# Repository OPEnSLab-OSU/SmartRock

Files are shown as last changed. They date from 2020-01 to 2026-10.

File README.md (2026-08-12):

# Smart Rock |<!-- [Updates](https://github.com/OPEnSLab-OSU/OPEnS-Lab-Home/wiki/smart-rock-updates) |--> [Wiki](https://github.com/OPEnSLab-OSU/SmartRock/wiki)
Project Leads: **Tyler Slaght**

Project Members; **Chris Milford**, **Owen Schwab**, **Max Emrich**

<!--Past Team Members **Annika Sundstorm** **Colin Hale-Brown**-->

Interested in the project? Email us at: slaghtt@oregonstate.edu

Smart rock aims to be a low cost, high accuracy, easy to use in-situ water quality measuring device. Our
goal with Smart Rock is to create an open source, low cost, and technically accessible hydrological sensor
suite. The intended result of this work allows data to be collected throughout a watershed; even in varied
and/or harsh conditions to improve system wide watershed knowledge.
Smart Rock could be used as a learning tool for students, teachers, and other citizen scientists. The
device currently costs ˜$350 in materials and takes approximately 4-8 hours to assemble and program.

Comprehensive Build Guide -> https://github.com/OPEnSLab-OSU/SmartRock/blob/master/Documentation/SmartRock_Guide-compressed.pdf

Smart Rock Paper -> https://github.com/OPEnSLab-OSU/SmartRock/blob/master/Documentation/SmartRock_Paper.pdf

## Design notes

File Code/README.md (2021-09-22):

## Software

For best results follow the table below for best code version:

Hardware Version | Software Version
------- | -------
Version 3 | Smartrock_firmware_v2.7
Version 2.5 | Smartrock_firmware_v2.5.1
Version 2.0 | Smartrock_firmware_v2.5.1

For best results use the following Arduino library versions for all versions of the code:

Board Package | Version
------ | ------
Arduino SAMD | 1.8.11
Adafruit SAMD | 1.5.7
Loom | 2.5.1

For info about installing Loom please visit the Loom [Github page](https://github.com/OPEnSLab-OSU/Loom) for details.

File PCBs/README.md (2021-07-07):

# Custom PCBs

Each Smart Rock contains three custom PCBs, the EC breakout board and OsmoPod can be found here. Information about the Hypnos Board can be found [Here](https://github.com/OPEnSLab-OSU/OPEnS-Lab-Home/wiki/Hypnos).

Board | Description
----- | -----
EC Breakout	| Module containing EC circuitry and breakout plugs for the other sensors.
OsmoPod | Module containing EC probes and MS5803 pressure/ temperature sensor.
Hypnos | Module for time, sleep, and data storage functionalities of the Smart Rock.

Please referance the correct PCB for your Smart Rock, board verions have changed as we have shipped.

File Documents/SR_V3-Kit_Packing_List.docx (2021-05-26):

Smart Rock V3 – Kit Parts List

OC | RC | Quantity | Photo | Item
| | 1 | | PVC Enclosure
| | 9 | | M3 Nut
| | 2 | | 8mm M3 Screw
| | 4 | | 10mm M3 Screw
| | 1 | | 3” Velcro Cable Tie
| | 1 | | Sled_Base
| | 1 | | Electronics_Mount
| | 1 | | Turbidity_Mount
| | 1 | | Battery_Mount
| | 1 | | Rail_Inside
| | 1 | | Rail_Outside
| | 1 | | Feather M0
| | 1 | | Hypnos
| | 1 | | EC Breakout Board
| | 1 | | 16GB Micro-SD Card
| | 1 | | Micro-SD Card to SD Card Adapter
| | 1 | | 3.3V 2200mAh Li-Po Battery
| | 1 | | Coin Cell Battery
| | 1 | | Li-Pi Battery Charger
| | 1 | | Smart Rock Faceplate
| | 2 | | Descant Packet
| | 1 | | Super Glue

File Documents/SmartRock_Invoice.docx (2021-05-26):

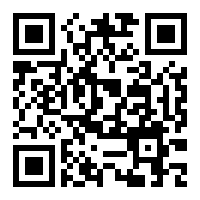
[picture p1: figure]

Smart Rock V3

Thank you for purchasing our latest revision of the Smart Rock. We have documented how to get started on the GitHub Wiki in the Operation Guide.

Contact: halebroc@oregonstate.edu

Quantity | Item

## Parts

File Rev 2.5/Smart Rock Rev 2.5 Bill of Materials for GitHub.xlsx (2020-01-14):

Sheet: Smart Rock Bill of Materials
Smart Rock Bill of Materials
Document updated/edited by: Sam Edwards and Alicia Veach
Most recent update: 10/10/2019

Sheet: Mechanical Components
Smart Rock Mechanical Components Bill of Materials
Section of Smart Rock | Smart Rock ID number | Item Description | Distributor part number | MFG part number | Quantity per 1 Smart Rock | Cost per 1 pcs | Cost Per 1 Smart Rock | Required Purchasing quantity | Cost for Required quantity | Product/site info | Notes | Total cost for one Smart Rock: | $60.24
Waterproof Case | M2-0801 | Union PVC Fittings | 457-025 | n/a | 2 | $13.93 | $27.86 | 1 | $13.93 | PVCFittingsOnline (https://www.pvcfittingsonline.com/2-1-2-sch-40-pvc-union-soc-w-buna-n-o-ring-seal-457-025.html) |  | w/o securing structure | $50.62
M3-0001 | M1-0103 | Acrylic (ends) | 8560K354 | n/a | 2 | $1.93 | $3.85 | 12"x12" | $17.34 | McMaster Carr (https://www.mcmaster.com/8560k354) | 92 mm diameter, 6 mm thickness 2 per rock =~ 1/4" thick for ordering purposes --> Cost division is approximate
 | M1-0101 | PVC Pipe | 48925K99 | n/a | 8 | $1.37 | $10.96 | 60" | $16.39 | McMasterCarr (https://www.mcmaster.com/48925k99) | qty per 1 rock is # of inches, 1pcs=1inch
Internal Structure | M2-0802 | Velcro hook squares | 9737K72 | n/a | 5 | $0.28 | $1.40 | 10 | $2.79 | McMaster (https://www.mcmaster.com/9737k72) | 5 per rock
M3-0002 | M2-0803 | Velcro loop squares | 9737K82 | n/a | 5 | $0.28 | $1.40 | 10 | $2.79 | McMaster (https://www.mcmaster.com/9737k82) | 5 per rock
 | M1-0301 | 3D printed rails | n/a | n/a | 1 | $4.00 | $4.00 | 1 | $4.00 | OPEnS (http://www.open-sensing.org/resources#form-2) | Asa print, 1 outside, 1 inside, cost comes from opens lab --> only service cost for the project.
 | M1-0102 | Acrylic (slide) | 8560K239 | n/a | 1 | $1.14 | $1.14 | 12"x12" | $9.15 | McMasterCarr (https://www.mcmaster.com/8560k239) | 50x195x4mm, laser cut, 1 per rock =~1/8"thick for ordering purposes --> Cost division is approximate
Securing Structure | M2-0901 | U-Bolt | 3035T55 | n/a | 2 | $4.81 | $9.62 | 1 | $4.81 | McMasterCarr (https://www.mcmaster.com/3035t55)
M3-0003

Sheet: Electrical Components
Smart Rock Electrical Components Bill of Materials
Section of Smart Rock | Smart Rock ID number | Item | Distributor part number | MFG part number | Quantity per 1 Smart Rock | Cost per 1 pcs | Cost per 1 Smart Rock | Required Purchasing quantity | Cost for Required quantity | Product/site info | Notes | Total cost for one Smart Rock: | $152.43
Pressure Sensor Assembly | E2-0101 | Pressure Sensor | 223-1623-5-ND | MS580302BA01-00 | 1 | $13.82 | $13.82 | 1 | $13.82 | Digikey (https://www.digikey.com/product-detail/en/te-connectivity-measurement-specialties/MS580301BA01-00/223-1623-5-ND/5277628)
E3-0001 | E2-0201 | 10k resistor | RR12P10.0KDCT-ND | RR1220P-103-D | 2 | $0.04 | $0.08 | 100 | $3.49 | Digikey (https://www.digikey.com/product-detail/en/susumu/RR1220P-103-D/RR12P10.0KDCT-ND/432854) | surface mount
 | E2-0301 | 100nF Capacitor | 1276-1007-1-ND | CL21F104ZBCNNNC | 1 | $0.03 | $0.03 | 100 | $2.03 | Digikey (https://www.digikey.com/product-detail/en/samsung-electro-mechanics/CL21F104ZBCNNNC/1276-1007-1-ND/3889093) | surface mount
Microcontroller Assembly | E2-0601 | Feather Wifi m0 |  | 2995 | 1 | $20.00 | $20.00 | 1 | $34.95 | Adafruit Product (https://www.adafruit.com/product/3061)
E3-0006 | E2-0505 | Stackable headers |  | 2830 | 2 | $0.50 | $2.00 | 1 | $0.50 | Adafruit (https://www.adafruit.com/product/2830)
 | E2-0506 | Break away male headers |  | 392 | 1 | $4.95 | $0.17 | 1 | $4.95 | Adafruit (https://www.adafruit.com/product/392) | 12 pins total needed, 360 per pack
Turbidity Sensor E3-0007 | E2-0102 | Turbidity Sensor | SEN0189 |  | 1 | $9.90 | $9.90 | 1 | $9.90 | DF Robot (https://www.dfrobot.com/product-1394.html)
pH Sensor |  | pH Sensor | SEN0169 |  | 1 | $56.90 | $56.90 | 1 | $56.90 | DF Robot (https://www.dfrobot.com/product-1110.html)
Battery | E2-1203 | Lithium-Ion Poly Battery | 328 |  | 1 | $14.95 | $14.95 | 1 | $14.95 | Adafruit Product (https://www.adafruit.com/product/328) | 3.7V, 2500mAh
Salinity assembly | E2-0103 | TDS Sensor Probe | SEN0244 |  | 1 | $12.90 | $12.90 | 1 | $12.90 | DF Robot (https://www.dfrobot.com/product-1662.html)
E3-0005
Hypnos assembly |  | n channel mosfet | DMN65D8L-7DICT-ND |  | 1 | $0.17 | $0.17 |  |  | Digikey (https://www.digikey.com/product-detail/en/diodes-incorporated/DMN65D8L-7/DMN65D8L-7DICT-ND/3677916)
$15.74 |  | p channel mosfet | DMP3099L-7DICT-ND |  | 2 | $0.33 | $0.66 |  |  | Digikey (https://www.digikey.com/products/en?keywords=DMP3099L-7DICT-ND)
 |  | 80k resistor 1% | A129833CT-ND |  | 1 | $0.10 | $0.10 |  |  | Digikey (https://www.digikey.com/product-detail/en/te-connectivity-passive-product/CRGCQ1206F82K/A129833CT-ND/8577665)
 |  | 100k resistor 1% | 311-100KCRCT-ND |  | 2 | $0.10 | $0.20 |  |  | Digikey (https://www.digikey.com/product-detail/en/yageo/RC0805FR-07100KL/311-100KCRCT-ND/730491)
 |  | 30k resistor 5% | P30KECT-ND |  | 4 | $0.10 | $0.40 |  |  | Digikey (https://www.digikey.com/product-detail/en/panasonic-electronic-components/ERJ-8GEYJ303V/P30KECT-ND/203313)
 |  | MicroSD card socket | 1660 |  | 1 | $1.95 | $1.95 |  |  | Adafruit (https://www.adafruit.com/product/1660)
 |  | DS3231 IC | DS3231SN#T&R |  | 1 | $8.77 | $8.77 |  |  | Digikey (https://www.digikey.com/products/en?keywords=DS3231SN%23T%26RCT-ND)
 |  | Push button | KMR731NG LFS |  | 2 | $0.34 | $0.68 |  |  | Digikey (https://www.digikey.com/product-detail/en/c-k/KMR731NG-LFS/CKN10687CT-ND/6035359)
 |  | Battery holder 12mm | 36-3000CT-ND |  | 1 | $0.91 | $0.91 |  |  | Digikey (https://www.digikey.com/product-detail/en/keystone-electronics/3000TR/36-3000CT-ND/1532229)
 |  | 10k resistor 1% | A130183CT-ND |  | 2 | $0.10 | $0.20 |  |  | Digikey (https://www.digikey.com/product-detail/en/te-connectivity-passive-product/CRGCQ1206J10K/A130183CT-ND/8578015)
 |  | 0.1uF capacitor | 311-1488-1-ND |  | 2 | $0.19 | $0.38 |  |  | Digikey (https://www.digikey.com/product-detail/en/yageo/CC1206KKX7R0BB104/311-1488-1-ND/2833794)
 |  | KingBright LED low current | 754-1935-1-ND |  | 2 | $0.51 | $1.02 |  |  | Digikey (https://www.digikey.com/product-detail/en/kingbright/APT2012LSECK-J3-PRV/754-1935-1-ND/5177465)
 |  | 3K ohm resistor 1% | RMCF1206FT3K00CT-ND |  | 1 | $0.10 | $0.10 |  |  | Digikey (https://www.digikey.com/product-detail/en/stackpole-electronics-inc/RMCF1206FT3K00/RMCF1206FT3K00CT-ND/2418728)
 |  | 6.2k ohm resistor 1% | 311-6.20KFRCT-ND |  | 1 | $0.10 | $0.10 |  |  | Digikey (https://www.digikey.com/product-detail/en/yageo/RC1206FR-076K2L/311-6.20KFRCT-ND/731963)
 |  | 100pF Capacitor | 399-1205-1-ND |  | 1 | $0.10 | $0.10 |  |  | Digikey (https://www.digikey.com/product-detail/en/kemet/C0805C101J5GACTU/399-1122-1-ND/411397)
 | E2-1202 | MicroSD Card with adapter |  |  | 1 | $4.99 | $4.99 | 1 | $4.99 | Amazon (https://www.amazon.com/SanDisk-Mobile-MicroSDHC-SDSDQM-B35A-Adapter/dp/B004ZIENBA?s=gateway)
 | E2-1201 | Coin cell battery |  | 380 | 1 | $0.95 | $0.95 | 1 | $0.95 | Adafruit Product (https://www.adafruit.com/product/380)

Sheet: PCBs
Smart Rock Electrical Components Bill of Materials
Section of Smart Rock | Smart Rock ID Number | Item | Quantity per Smart Rock | Cost Per 1 Smart Rock | Required Purchasing Quantity | Cost for required quantity | Product site/info | notes | Total cost for one Smart Rock: | $9.43
Pressure Sensor | E2-0701 | Pressure Sensor PCB | 1 | $0.48 | 3 | $1.45 | OSH Park
Hydro PCB | E2-0703 | Base PCB | 1 | $5.50 | 3 | $16.50 | OSH Park
Hypnos | E2-0704 | Hypnos | 1 | $3.45 | 3 | $10.35 | OSH Park

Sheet: Bulk Materials
Smart Rock Bulk Materials Bill of Materials
(materials that can not have calculated quantities per 1 Smart Rock)
Section of Smart Rock | Smart Rock ID number | Item | Distributor part number | MFG part number | Required Purchasing quantity | Cost for Required quantity | Product/site info | Notes
Waterproof Case | M1-0201 | Epoxy | N/A | N/A | 1 tube 0.85 oz | $7.17 | Amazon (https://www.amazon.com/Loctite-1919324-0-85-Fluid-Syringe-1405604/dp/B00KH62K50?hvadid=77790515638846&hvbmt=be&hvdev=c&hvqmt=e&s=gateway)
Waterproof Case | M1-0202 | Silicone Grease | N/A | 92003 | 1 tube 3 oz | $9.79 | Amazon (https://www.amazon.com/Super-Lube-92003-Lubricating-Translucent/dp/B0081JE0OO?s=gateway&srs=3044028011)
Waterproof Case | M1-0203 | PVC Cement | N/A | 31133 | 1can 16oz | $16.43 | Amazon (https://www.amazon.com/Oatey-31133-Weather-Cement-32-Ounce/dp/B000BVS08C?th=1)
Waterproof Case | M1-0204 | PVC Primer | 18815K51 | N/A | 1can 8oz | $6.07 | McMasterCarr (https://www.mcmaster.com/18815k51)
Pressure Sensor | E1-0201 | Lead Free Solder Paste | TS391SNL-ND | TS391SNL | 1 | $16.95 | Digikey (https://www.digikey.com/product-detail/en/chip-quik-inc/TS391SNL/TS391SNL-ND/7802215) | 12 month shelf life
Solder stock | E1-0202 | Rosin Flux-Core Solder | 7659A41 |  | 1 | $4.81 | McMaster-Carr (https://www.mcmaster.com/7659a41)
Wiring | E1-0101 | Female dupont wire |  |  | 1 pack | $9.99 | Amazon (https://www.amazon.com/KABUDA-Multicolored-Dupont-Breadboard-Arduino/dp/B07QXXMWRZ?s=gateway) | 40 pin male, 40 pin female
Battery |  | Battery Charger | 1304 |  | 1 | $5.95 | Adafruit (https://www.adafruit.com/product/1304)
Internal Structure | M1-0205 | Super Glue |  | 7805001 | 1 0.53oz container | $2.99 | #VALUE! (https://www.amazon.com/Gorilla-Super-Glue-Gram-Clear/dp/B001IY82FM?hvadid=193151859311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)
 |  |  |  |  |  | $71.21

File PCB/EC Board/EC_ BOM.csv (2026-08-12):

Qty | Value | Device | Package | Parts | Description | ARROW_PART_NUMBER | ARROW_PRICE-STOCK | AVAILABILITY | CATEGORY | COPYRIGHT | CURRENT_RATING | DATASHEET | DESCRIPTION | FORWARD_CURRENT | FORWARD_VOLTAGE | HEIGHT | MANUFACTURER | MANUFACTURER_NAME | MANUFACTURER_PART_NUMBER | MATERIAL_CORE | MF | MFR_NAME | MOUSER_PART_NUMBER | MOUSER_PRICE-STOCK | MP | MPN | OPERATING_TEMP | OPERATING_TEMPERATURE | PACKAGE | PACKAGE_SIZE | PACKAGE_TYPE | PART_STATUS | POPULARITY | PRICE | RATING | REFDES | REVERSE_VOLTAGE | ROHS | ROHS_COMPLIANT | SERIES | SUB-CATEGORY | SUBCATEGORY | TEMPERATURE_COEFFICIENT | THERMALLOSS | TOLERANCE | TYPE | VOLTAGE_RATING | ZENER_VOLTAGE
3 |  | PINHD-1X4 | 1X04 | JP1, JP2, JP3 | PIN HEADER |  |  |  |  |  |  |  |  |  |  |  |  |  |  |  |  |  |  |  |  |  |  |  |  |  |  |  | 91
5 | 100k | R-US_CHIP-0402(1005-METRIC) | RESC1005X40 | R3, R6, R13, R14, R15 | Resistor Fixed - ANSI |  |  |  | Resistor |  |  |  |  |  |  |  |  |  |  |  |  |  |  |  |  |  |  |  |  |  |  |  |  |  |  |  |  |  |  |  | Fixed
4 | 10k | R-US_CHIP-0402(1005-METRIC) | RESC1005X40 | R1, R5, R11, R12 | Resistor Fixed - ANSI |  |  |  | Resistor |  |  |  |  |  |  |  |  |  |  |  |  |  |  |  |  |  |  |  |  |  |  |  |  |  |  |  |  |  |  |  | Fixed
1 | 10k | R-US_CHIP-1206(3216-METRIC) | RESC3216X70 | SHUNT | Resistor Fixed - ANSI |  |  |  | Resistors |  |  |  | Chip Resistor 3.20 X 1.60 X 0.70 mm body 1206(3216-METRIC) Package |  |  |  |  |  |  |  |  |  |  |  |  |  |  |  |  | 1206 | Surface Mount
6 | 1k | R-US_CHIP-0402(1005-METRIC) | RESC1005X40 | R2, R4, R7, R8, R9, R10 | Resistor Fixed - ANSI |  |  |  | Resistor |  |  |  |  |  |  |  |  |  |  |  |  |  |  |  |  |  |  |  |  |  |  |  |  |  |  |  |  |  |  |  | Fixed
2 | 1nF | C_CHIP-0402(1005-METRIC) | CAPC1005X60 | C13, C14 | Capacitor - Generic |  |  |  | Capacitor
16 | 1uF | C_CHIP-0402(1005-METRIC) | CAPC1005X60 | C1, C2, C3, C4, C9, C10, C11, C12, C15, C16, C17, C18, C19, C20, C21, C22 | Capacitor - Generic |  |  |  | Capacitor
2 | 4.7uF | C_CHIP-0402(1005-METRIC) | CAPC1005X60 | C7, C8 | Capacitor - Generic |  |  |  | Capacitor
1 | 68 uH | L_CHIP-0805(2012-METRIC) | INDC2009X120 | L1 | Inductor Fixed - Generic |  |  |  | Inductors |  |  |  | Chip 2.00 X 0.90 X 1.20 mm body 0805(2012-METRIC) |  |  |  |  |  |  |  |  |  |  |  |  |  |  |  |  | 0805 | Surface Mount
1 | 74AUP1T08GWH | 74AUP1T08GWH | SOT65P212X110-5N | IC1 | 74AUP1T08 - Low-power 2-input AND gate with voltage-level translator@en-us | 74AUP1T08GWH | https://www.arrow.com/en/products/74aup1t08gwh/nexperia?region=nac |  |  |  |  |  | 74AUP1T08 - Low-power 2-input AND gate with voltage-level translator@en-us |  |  | 1.1mm |  | Nexperia | 74AUP1T08GWH |  |  |  | 771-74AUP1T08GWH | https://www.mouser.co.uk/ProductDetail/Nexperia/74AUP1T08GWH?qs=chTDxNqvsynKkpBm9IAgCA%3D%3D
2 | 865090640004CAP_WCAP-ASLU_04P0X05P5_WRE-L | 865090640004CAP_WCAP-ASLU_04P0X05P5_WRE-L | CAP_WCAP-ASLU_04P0X05P5_WRE-L | C5, C6 |  |  |  |  |  | Copyright (C) 2024 Ultra Librarian. All rights reserved. |  |  |  |  |  |  |  |  | 865090640004 |  |  | Wurth Electronics
1 | ADAFRUIT_FEATHERWING | ADAFRUIT_FEATHERWING | ADAFRUIT_FEATHERWING | MS1
1 | ADS1115IDGSRDGS0010A_L | ADS1115IDGSRDGS0010A_L | DGS0010A_L | U2 |  |  |  |  |  | Copyright (C) 2024 Ultra Librarian. All rights reserved. |  |  |  |  |  |  |  |  | ADS1115IDGSR |  |  | Texas Instruments |  |  |  |  |  |  |  |  |  |  |  |  |  | RefDes |  |  |  |  |  |  |  |  |  | TYPE
1 | CD4060BPWR | CD4060BPWR | CD4060BPWR | U4
2 | DIODE_1N4004_DO41-10 | DIODE_1N4004_DO41-10 | DO41-10 | D1, D2 | Diode Rectifier - Popular Parts |  |  |  | Diode |  |  | https://www.onsemi.com/pdf/datasheet/1n4001-d.pdfv | Diode 400 V 1A Through Hole DO-41 | 1 A | 1.1 V |  | onsemi |  |  |  |  |  |  |  |  | 1N4004 |  | -55°C ~ 175°C |  | DO-41 | Through Hole | Obsolete |  |  |  |  | NA | Compliant |  | 1N4004 |  | Rectifiers |  |  |  | Single Diodes |  | NA
1 | MAX4678EUE+ | MAX4678EUE+ | SOP65P640X110-16N | U5
2 | OP747ARUZ-REELRU_14_ADI | OP747ARUZ-REELRU_14_ADI | RU_14_ADI | U1, U10 |  |  |  |  |  | Copyright (C) 2024 Ultra Librarian. All rights reserved. |  |  |  |  |  |  |  |  | OP747ARUZ-REEL |  |  | Analog Devices Inc
1 | PINHD-1X06_1X06M | PINHD-1X06_1X06M | 1X06 | U$1
1 | TPS60400DBVR | TPS60400DBVR | SOT95P280X145-5N | U6 | Unregulated 60mA charge pump Voltage Inverter |  |  | Unavailable |  |  |  |  | 60mA Charge Pump Voltage Inverter with Variable Switching Frequency 5-SOT-23 -40 to 85 |  |  |  |  |  |  |  | Texas Instruments |  |  |  | TPS60400DBVR |  |  |  | SOT-23-5 Texas Instruments |  |  |  |  | None
3 | US1G-E3/61T | DIODE_US1G-E3/61T_SMA | DIOM5226X290N | D9, D10, D11 | Diode Rectifier - Popular Parts |  |  |  | Diode |  |  | https://www.vishay.com/docs/88768/us1_test_dcicons.pdf | Diode 400 V 1A Surface Mount DO-214AC (SMA) | 1A | 1V |  | Vishay General Semiconductor - Diodes Division |  |  |  |  |  |  |  |  | US1G-E3/61T |  | -55°C ~ 150°C |  | SMA | Surface Mount | Active |  |  |  |  | 400V | Compliant |  | US1 |  | Rectifiers |  |  |  | Fast Recovery Rectifiers |  | NA

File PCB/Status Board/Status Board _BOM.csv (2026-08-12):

Reference Designators | Quantity | Description | Package | Value | Manufacturer | Manufacturer Part Number | Vendor | Vendor Part Number | Top/Bottom
 | 1 | Board | Board
C1, C2 | 2 | Capacitor - Generic | CAPC2012X110 | 1uF |  |  |  |  | Top
C5 | 1 | Capacitor - Generic | CAPC2012X110 | 100nF |  |  |  |  | Top
I2C#1-SOLDERPADS, LED_SOLDERPADS | 2 |  | 1X04 | PINHD-1X04_1X04M |  |  |  |  | Top
LED1_ALWAYS-ON, LED2_READING, LED3_BLUETOOTH_READING | 3 |  | LED_LSM0805_2P0X1P25X0P8_VCC | LSM0805543VLED_LSM0805_2P0X1P25X0P8_VCC |  |  |  |  | Top
R1, R2, R3 | 3 | Resistor Fixed - Generic | RESC2012X65 | 2.2k |  |  |  |  | Top
R5 | 1 | Resistor Fixed - Generic | RESC2012X65 | 10k |  |  |  |  | Top
REED_SWITCH_HOLE | 1 |  | 1X02 | PINHD-1X02_1X02M |  |  |  |  | Top
U2 | 1 |  | MS5803-02BA01_TEC | MS580302BA01-00MS5803-02BA01_TEC |  |  |  |  | Top
U3 | 1 | Check availability | PHODET_VCNL4020 | VCNL4020-GS08 |  |  |  |  | Top

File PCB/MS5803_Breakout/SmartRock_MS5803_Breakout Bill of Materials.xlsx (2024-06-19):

EAGLE Board # | Part | Part Number | Footprint/Package | Quantity/Board | Source (Link)
U1 | Pressure/Temp Sensor | MS580302BA01-00 | 8-SMD Module | 1 | Digikey (https://www.digikey.com/en/products/detail/te-connectivity-measurement-specialties/MS580302BA01-00/5277629)
C1 | 0.1 uF Ceramic Cap | CL21F104ZBANNNC | 0805 (2012 Metric) | 1 | Digikey (https://www.digikey.com/en/products/detail/samsung-electro-mechanics/CL21F104ZBANNNC/3889200)

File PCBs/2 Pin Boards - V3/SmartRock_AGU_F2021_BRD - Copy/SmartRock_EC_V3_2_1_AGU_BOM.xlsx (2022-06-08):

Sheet: BOM
Board Label | Value | Item Description | Quantity Given | Quantity per Device | Cost per Unit | Cost per Device | Product Site | Manufacturer ID | Packaging/Case | Type | Notes | Alternative Source
JP1 | 12 Pin (Female) | CONN HDR 12POS 0.1 TIN PCB | 1 | 1 | $0.78 |  | Digikey (https://www.digikey.com/en/products/detail/sullins-connector-solutions/PPTC121LFBN-RC/807231) | S6100-ND | Tray
JP2 + JP3 | 16 Pin (Female) | CONN HDR 16POS 0.1 TIN PCB | 1 | 1 | $0.98 |  | Digikey | S7014-ND | Tray
JP5 | 3 Pin (Male) | CONN HEADER VERT 3POS 2.54MM | 1 | 1 | $0.13 |  | Digikey (https://www.digikey.com/en/products/detail/w%C3%BCrth-elektronik/61300311121/4846825) | 732-5316-ND | Tray |  | OOS
CN1 | 2 Pin 2.5mm JST | CONN HEADER VERT 2POS 2MM | 1 | 1 | $0.17 |  | Digikey (https://www.digikey.com/en/products/detail/jst-sales-america-inc/B2B-PH-K-S(LF)(SN)/926611) | 455-1704-ND | Bulk |  | OOS
CN2 | 3 Pin 2.5mm JST | CONN HEADER VERT 3POS 2MM | 1 | 1 | $0.19 |  | Digikey (https://www.digikey.com/en/products/detail/jst-sales-america-inc/B3B-PH-K-S-LF-SN/926612) | 455-1705-ND | Bulk |  | OOS
CN3 | 4 Pin 2.5mm JST | CONN HEADER VERT 4POS 2MM | 1 | 1 | $0.24 |  | Digikey (https://www.digikey.com/en/products/detail/jst-sales-america-inc/B4B-PH-K-S-LF-SN/926613) | 455-1706-ND | Bulk |  | OOS
U1 | ADS1115 | IC ADC 16BIT SIGMA-DELTA 10VSSOP | 1 | 1 | $6.38 |  | Digikey (https://www.digikey.com/en/products/detail/texas-instruments/ADS1115IDGST/2123298) | IC ADC 16BIT SIGMA-DELTA 10VSSOP | Cut Tape/VSSOP |  | OOS
U2 | 3.3V Inverter | IC REG CHARG PUMP INV 60MA SOT23 | 1 | 1 | $1.14 |  | Digikey (https://www.digikey.com/en/products/detail/texas-instruments/TPS60400DBVR/1672052) | 296-27004-1-ND - Cut Tape | Cut Tape/SOT-753 |  | OOS
U3 | Op-Amp | IC OPAMP JFET 4 CIRCUIT 14DIP | 1 | 1 | $0.85 |  | Digikey (https://www.digikey.com/en/products/detail/texas-instruments/TL074CN/277423) | 296-1777-ND | Tube/14-PDIP |  | OOS
S1 | SPDT Switch | SWITCH SLIDE SPDT 200MA 30V | 1 | 1 | $0.76 |  | Digikey (https://www.digikey.com/en/products/detail/e-switch/EG1218/101726) | EG1903-ND | Bulk
D1,D2,D3,D4,D5 | 1N4001 Diodes |  |  |  |  |  |  |  |  |  | Good to Go
C1,C2,C3 | 100nF
C4,C5,C6,C7,C8,C9,C10 | 1uF
R1,R4,R6,R17 | 1k |  |  |  |  |  | Digikey (https://docs.google.com/spreadsheets/d/1rMLxxit3fiBuBLfVr-LG5nceliVDEqr13rMm8BmzxTA/edit) |  |  |  | Already Thick Film
R5 | 2k |  |  |  |  |  | Digikey (https://www.digikey.com/en/products/detail/yageo/RC1206JR-072KL/732183) |  |  |  | Already Thick Film
R8,R11,R18,R19 | 4.7k |  |  |  |  |  | Digikey (https://www.digikey.com/en/products/detail/yageo/RC1206FR-074K7L/731834) |  |  |  | Already Thick Film
R10 | 5k(4.99k) |  |  |  |  |  | Digikey (https://www.digikey.com/en/products/detail/vishay-dale/RCS12064K99FKEA/10059723) |  |  |  | Updated to Thick Film
R2,R7,R9,R14,R15 | 10k |  |  |  |  |  |  |  |  |  | Already Thick Film
R3 | 22k |  |  |  |  |  |  |  |  |  | Already Thick Film
LED1,LED2,LED3

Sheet: OPEnS Order Format
Date Needed | Ship To | Requester | Source | Description | Units | Part Number | Price/unit | Total | Purpose: X for Y | Notes | Project | Alternative Suppliers | Order Date
 | the Lab | Cameron W |  |  |  |  |  |  |  |  | SmartRock

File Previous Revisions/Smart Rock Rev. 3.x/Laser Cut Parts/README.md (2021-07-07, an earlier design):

## Laser Cut Parts

For the construction of one Smart Rock you need one of each of these parts. They are laser cut from extruded acrylic sheets.

Part | Material Thickness 
------ | ------
Sensor_Mount | 1/4"
Sled_Base | 1/8"
Electronics_Mount | 1/8"
Turbidity_Mount | 1/8"
MG5803_Shield | 1/16"

If your Smart Rock uses a 3D Printed rail please referance the for files marked Version 3. Otherwise use the files marked Version 3.1

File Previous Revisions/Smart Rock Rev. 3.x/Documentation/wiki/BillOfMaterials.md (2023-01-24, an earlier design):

# Bill Of Materials

This is the complete bill of materials for the different kit types. For info about the materials and assembly of "in house" parts please visit their corresponding wiki pages.

Kits | Type
---- | ----
A | Fully Assembled
B | To be Assembled
C | In house parts only

**Mechanical**

_For laser cut parts, the links provided are for raw material used. Not the part itself._

Item Description | Notes | Quantity per 1 SR | Part Number | Dist. Website | In kits 
------ | ------ | ------ | ------- | ------ | ------ 
Sled_Base | Laser cut from 1/8" extruded acrylic. | 1 | #### | [McMasterCarr](https://www.mcmaster.com/8589K43/) | A,B,C
Electronics_Mount | Laser cut from 1/8" extruded acrylic. | 1 | #### | [McMasterCarr](https://www.mcmaster.com/8589K43/) | A,B,C
Turbidity_Mount | Laser cut from 1/8" extruded acrylic. | 1 | #### | [McMasterCarr](https://www.mcmaster.com/8589K43/) | A,B,C
3" Velcro Cable Tie |  | 1 | 4330221319 | [Amazon](https://www.amazon.com/dp/B00QMMKY8I/) | A,B
Battery_Mount | 3D Printed | 1 | #### |  | A,B,C
Turbidity_Cover | 3D Printed | 1 | #### |  | A,B,C
Rail_Outside | 3D Printed | 1 | #### |  | A,B,C
Rail_Inside | 3D Printed | 1 | #### |  | A,B,C
8mm M3 Screw |  | 2 | 91292A112 | [McMasterCarr](https://www.mcmaster.com/91292a112) | A,B
10mm M3 Screw |  | 4 | 91292A113 | [McMasterCarr](https://www.mcmaster.com/91292A113/) | A,B
M3 Nut |  | 10 | 91828A211 | [McmasterCarr](https://www.mcmaster.com/91828A211/) | A,B

**Electrical**

Item Description | Notes | Quantity per 1 SR | Part Number | Dist. Website | In kits 
------ | ------ | ------ | ------- | ------ | ------ 
Feather M0 Basic Proto | Microcontroller | 1 | 2772 | [Adafruit](https://www.adafruit.com/product/2772) | A,B
Hypnos Board | Data logging, system power, real time clock. | 1 | #### |  | A,B,C
EC Breakout Board | Main Board | 1 | #### |  | A,B,C
MicroSD Card with adapter | For storing data in Hypnos. | 1 | #### | [Amazon](https://www.amazon.com/SanDisk-Mobile-MicroSDHC-SDSDQM-B35A-Adapter/dp/B004ZIENBA/) | A,B
CR1220 Coin Cell | For keeping time when battery is removed. | 1 | 54ZU79 | [Grainger](https://www.grainger.com/product/GRAINGER-APPROVED-1220-54ZU79) | A,B
Battery Charger | Charge lipo battery cell | 1 | 1304 | [Adafruit](https://www.adafruit.com/product/1304) | A,B
Lithium Ion Battery | 3.7V 2200mAh | 1 | 1781 | [Adafruit](https://www.adafruit.com/product/1304) | A,B
3-pin JST Cable | 100mm long | 1 | 4336 | [Adafruit](https://www.adafruit.com/product/4336) | A,B
Turbidity Breakout Board | Comes with turbidity sensor | 1 |  | [DFRobot]() | A,B

**Acrylic Face Plate**

Item Description | Notes | Quantity per 1 SR | Part Number | Dist. Website | In kits 
------ | ------ | ------ | ------- | ------ | ------ 
Acrylic_Faceplate | Laser cut from 1/4" extruded acrylic. | 1 | #### | [McMasterCarr](https://www.mcmaster.com/8560K357/) | A,B,C
OsmoPod | MS5803 and EC | 1 | #### |  | A,B,C
Turbidity Sensor |  | 1 | SEN0189 | [DF Robot](https://www.dfrobot.com/product-1394.html) | A,B

**PVC Enclosure**

Item Description | Notes | Quantity per 1 SR | Part Number | Dist. Website | In kits 
------ | ------ | ------ | ------- | ------ | ------ 
PVC Pipe (Quantity in inches) | 2.5" pipe | 4.125 | 5AFJ8 | [Grainger](https://www.grainger.com/product/GRAINGER-APPROVED-Pipe-5AFJ8?) | A,B
PVC Union Fitting | Only part of the fitting is used, cemented onto pipe | 1 | 457-025 | [SupplyHouse](https://www.supplyhouse.com/Spears-457-025-2-1-2-PVC-Sch-40-Socket-Union-w-Buna-N-O-ring) | A,B
PVC Cap Fitting | Cemented onto pipe | 1 | 447-025 | [SupplyHouse](https://www.supplyhouse.com/Spears-447-025-2-1-2-PVC-Schedule-40-Cap) | A,B

**Assembly, Calibration, and Deployment**

Item Description | Notes | Quantity per 1 SR | Part Number | Dist. Website | In kits 
------ | ------ | ------ | ------- | ------ | ------ 
Super Glue |
30 mL Cups |
3 mL Pipette
DI Rinse Pouch |
10 μS/cm calibration pouch |
447 μS/cm calibration pouch |
1213 μS/cm calibration pouch |
Desicant Packets |

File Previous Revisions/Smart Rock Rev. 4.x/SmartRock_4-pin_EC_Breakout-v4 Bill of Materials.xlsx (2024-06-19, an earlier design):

EAGLE Board # | Part | Part Number | Footprint/Package | Quantity/Board | Source (Link)
U2,U3,U4 | Quad OPAMP IC | TL074CPWR | 14TSSOP | 3 | Digikey (https://www.digikey.com/en/products/detail/texas-instruments/TL074CPWR/378454)
U1 | Binary Counter IC | CD4060BPWR | 16TSSOP | 1 | Digikey (https://www.digikey.com/en/products/detail/texas-instruments/CD4060BPWR/525925)
U5 | 16 bit ADC IC | ADS1115BQDGSRQ1 | 10VSSOP | 1 | Digikey (https://www.digikey.com/en/products/detail/texas-instruments/ADS1115BQDGSRQ1/6575621)
U6+ | Charge Pump Inverter IC | MAX660MX/NOPB | 8SOIC | 1 | Digikey (https://www.digikey.com/en/products/detail/texas-instruments/MAX660MX-NOPB/413263)
C1,C2 | 1 uF Electrolytic Cap | UPS1H010MDD1TD | Radial, Can (though hole) | 2 | Digikey (https://www.digikey.com/en/products/detail/nichicon/UPS1H010MDD1TD/4319731)
C3, C5 | 100 uF Electrolytic Cap | 10YXF100MEFCT15X11 | Radial, Can (though hole) | 2 | Digikey (https://www.digikey.com/en/products/detail/rubycon/10YXF100MEFCT15X11/3567031)
C4 | 1 nF Ceramic Cap | 1206GC102KAT2A | 1206 (3216 metric) SMD | 1 | Digikey (https://www.digikey.com/en/products/detail/kyocera-avx/1206GC102KAT2A/3247523)
C8,C9,C10 | 1 uF Ceramic Cap | C1206C105K5REC7210 | 1206 (3216 metric) SMD | 3 | Digikey (https://www.digikey.com/en/products/detail/kemet/C1206C105K5REC7210/8645630)
D1,D2,D3,D4 | 1N4001 Diode | 1N4001-G | DO-204AL, DO-41, Axial (through hole) (https://www.digikey.com/en/products/filter/diodes/rectifiers/single-diodes/do-204al-do-41-axial/280) | 4 | Digikey (https://www.digikey.com/en/products/detail/comchip-technology/1N4001-G/1979675)
R2, R3, R5, R6 | 1k ohm resistor 1% | RC1206FR-071KL | 1206 (3216 metric) SMD | 4 | Digikey (https://www.digikey.com/en/products/detail/yageo/RC1206FR-071KL/728387)
R1, R4, R16 | 3.3k ohm resistor 1% | RC1206FR-073K3L | 1206 (3216 metric) SMD | 3 | Digikey (https://www.digikey.com/en/products/detail/yageo/RC1206FR-073K3L/728766)
R8, R15 | 1M ohm resistor 1% | RC1206FR-071ML | 1206 (3216 metric) SMD | 2 | Digikey (https://www.digikey.com/en/products/detail/yageo/RC1206FR-071ML/728388)
R7, R9, R10, R11, R12, R13 | 10k ohm resistor 1% | RC1206FR-0710KL | 1206 (3216 metric) SMD | 6 | Digikey (https://www.digikey.com/en/products/detail/yageo/RC1206FR-0710KL/728483)
R14 | 100k ohm resistor 1% | RC1206FR-07100KL | 1206 (3216 metric) SMD | 1 | Digikey (https://www.digikey.com/en/products/detail/yageo/RC1206FR-07100KL/728492)
TUNING_RESISTOR | 200 ohm resistor 1% | RC1206FR-07200RL | 1206 (3216 metric) SMD | 1 | Digikey (https://www.digikey.com/en/products/detail/yageo/RC1206FR-07200RL/728675?s=N4IgTCBcDaIMwEYEFowAY0DEBKBhAKsgHIAiIAugL5A)

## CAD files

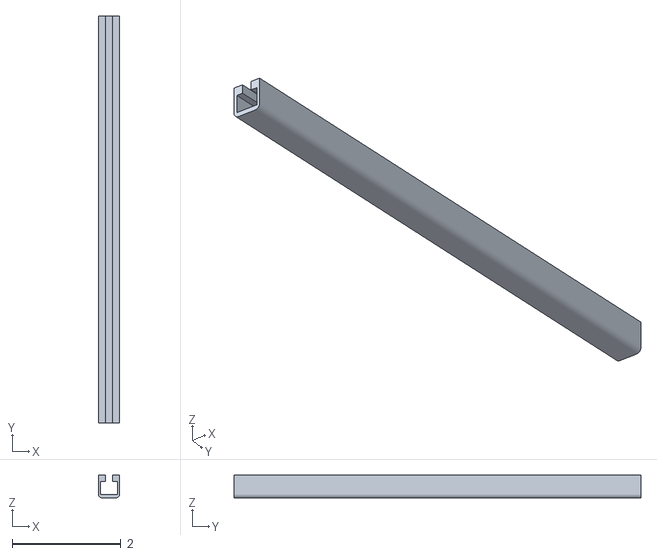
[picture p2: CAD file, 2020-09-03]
3D Printed Parts/Outside.stl
0.394 x 7.50 x 0.422

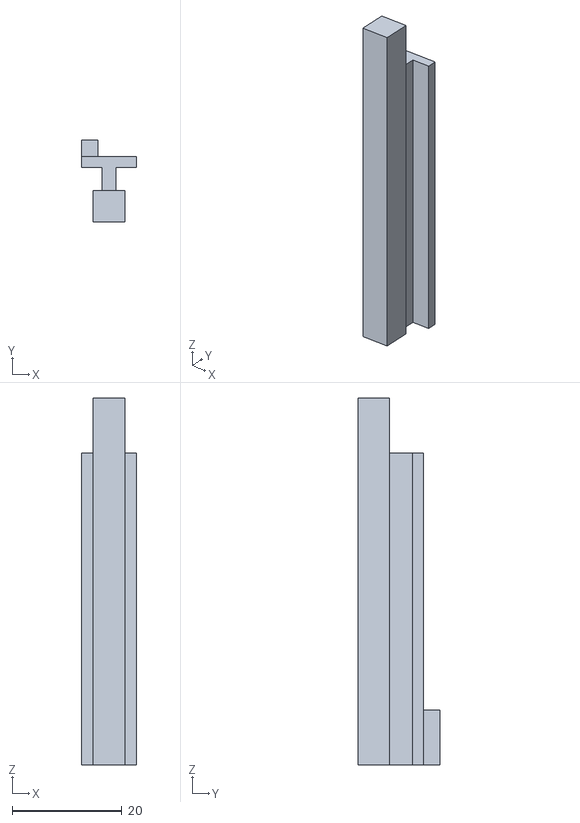
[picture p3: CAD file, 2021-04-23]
3D Prints/Rail_Inside v18.stl
10.0 x 15.0 x 67.0

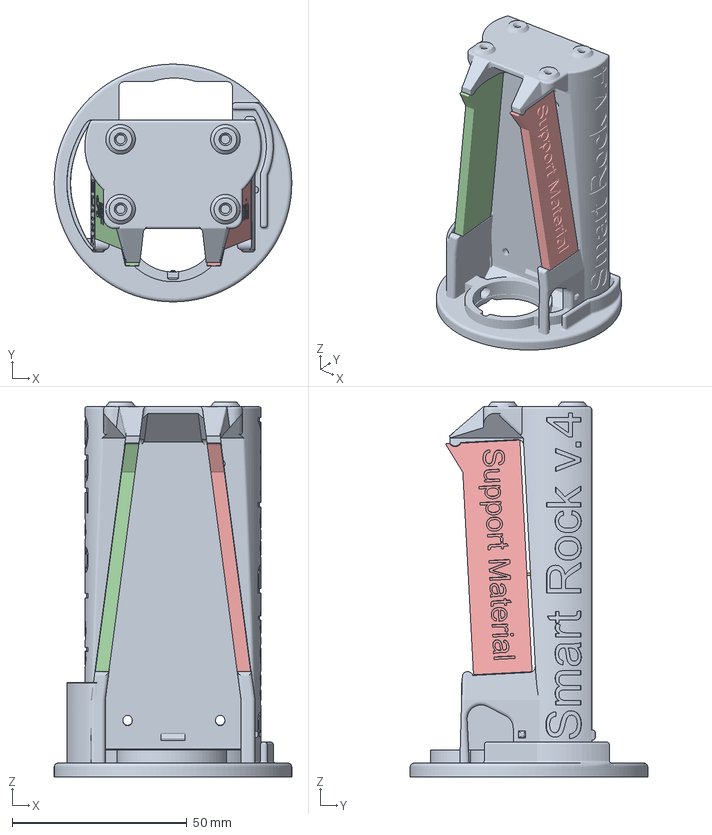
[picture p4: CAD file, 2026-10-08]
Build Files/3D Print Files/~Circuit Mount~.3mf
68.0 x 68.0 x 107.3 mm

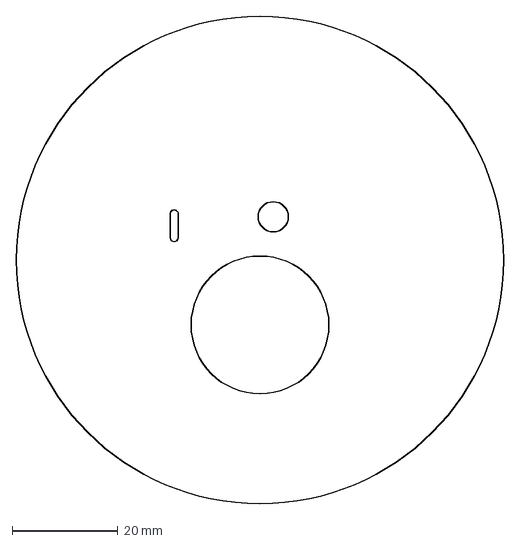
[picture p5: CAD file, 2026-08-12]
Build Files/Laser Cut Files/Faceplate.dxf
92.0 x 92.0 mm

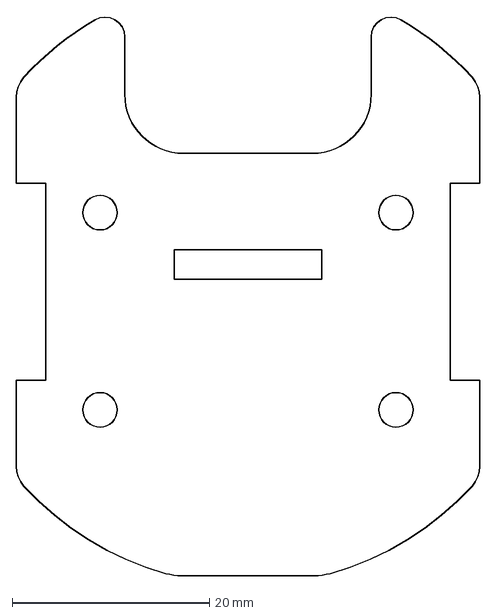
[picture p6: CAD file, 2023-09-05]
Laser Cut Parts/10000mAh Verson/SR_InternalSupport_v27_1x3mm.dxf
47.0 x 56.7 mm

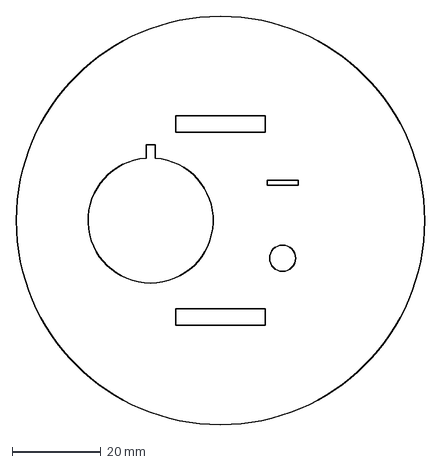
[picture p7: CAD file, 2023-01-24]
Laser Cut Parts/SR_SensorFacePlate_v24_1x6mm.dxf
92.0 x 92.0 mm

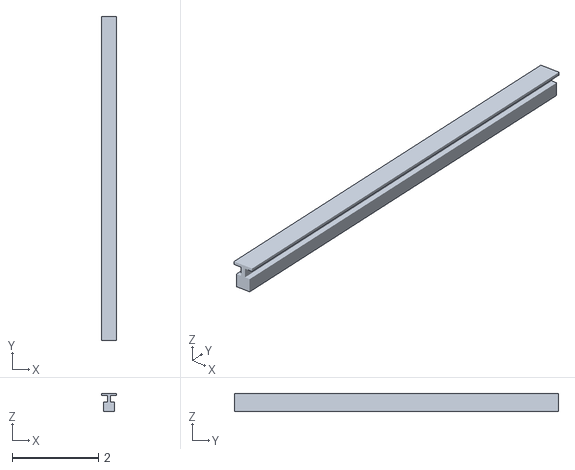
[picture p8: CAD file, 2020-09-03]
3D Printed Parts/Inside.stl
0.346 x 7.50 x 0.42

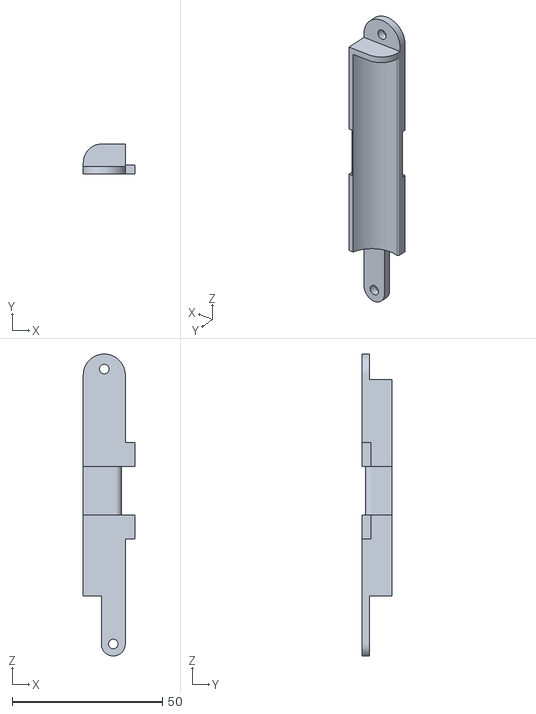
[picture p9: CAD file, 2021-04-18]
3D Prints/Battery_Mount v18.stl
17.1 x 10.0 x 100.5

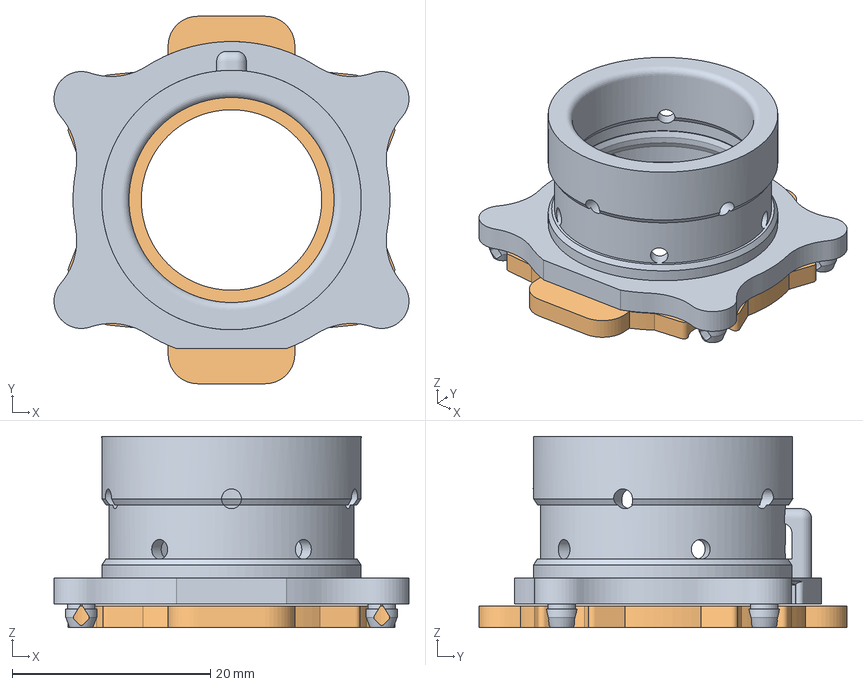
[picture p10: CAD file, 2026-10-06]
Build Files/3D Print Files/~Silicone Sinch~.3mf
35.8 x 37.1 x 19.3 mm

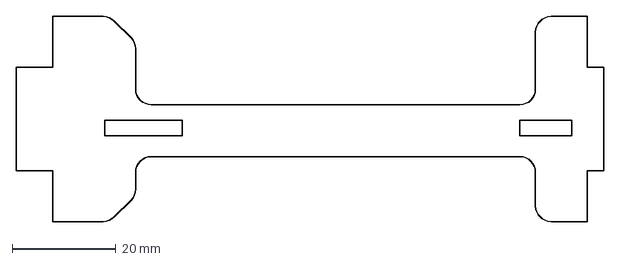
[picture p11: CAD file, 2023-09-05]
Laser Cut Parts/10000mAh Verson/SR_StructureArm_v31_1x3mm.dxf
113.2 x 39.5 mm

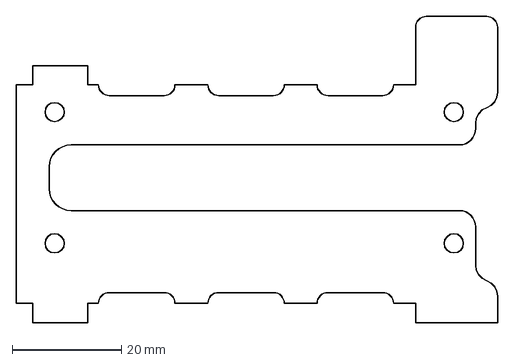
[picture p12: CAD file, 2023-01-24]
Laser Cut Parts/SR_MountPlate_v30_1x3.5mm.dxf
88.0 x 56.0 mm

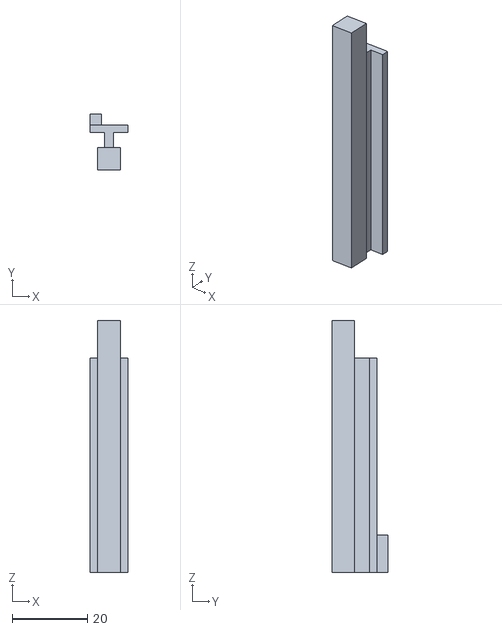
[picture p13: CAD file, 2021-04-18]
3D Prints/Rail_Inside v16.stl
10.0 x 15.0 x 67.0

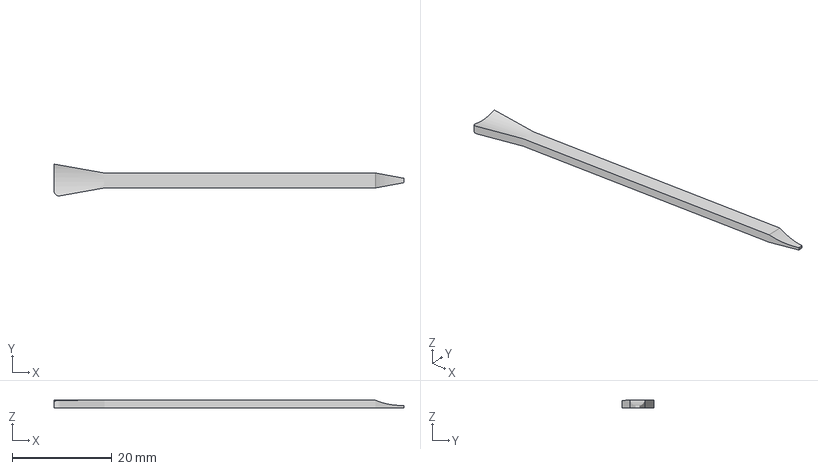
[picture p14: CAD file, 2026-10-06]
Build Files/3D Print Files/Clear Epoxy Stick.3mf
70.0 x 6.37 x 1.50 mm

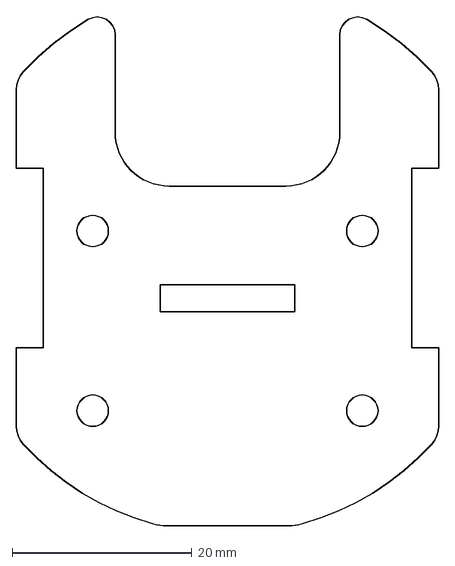
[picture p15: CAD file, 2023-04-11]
Laser Cut Parts/10000mAh Verson/SR_InternalSupport_v17_1x3mm.dxf
47.0 x 56.7 mm

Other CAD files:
Laser Cut Parts/SR_StructureArm_v16_1x3.5mm.dxf
3D Prints/Rail_Outside v13.stl
Laser Cut Parts/10000mAh Verson/SR_SensorFacePlate_v28_1x6.35mm.dxf
Laser Cut Parts/SR_InternalSupport_v13_1x3.5mm.dxf
3D Prints/Turbidity_Cover V5.stl
Build Files/3D Print Files/Acylic Locator.3mf
Build Files/3D Print Files/Clear Epoxy Mixing Cup.3mf
Build Files/3D Print Files/Status Board Locator.3mf
Build Files/3D Print Files/~U-bolt Mount~.3mf
Laser Cut Parts/10000mAh Verson/SR_MountPlate_v34_1x3mm.dxf
Laser Cut Parts/10000mAh Verson/SR_StructureArm_v23_1x3mm.dxf
Laser Cut Parts/Electronics_Mount v15.dxf
Laser Cut Parts/Electronics_Mount v26.dxf
Laser Cut Parts/OsmoPod_Shield v13.dxf
Laser Cut Parts/SR_Faceplate v16.dxf
Laser Cut Parts/SR_SensorShield_v12_1x3mm.dxf
Laser Cut Parts/Sensor_Mount v12.dxf
Laser Cut Parts/Sled_Base v20.dxf
Laser Cut Parts/Sled_Base v27.dxf
Laser Cut Parts/Sled_Base v28.dxf
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

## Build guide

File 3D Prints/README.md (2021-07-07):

## 3D Printed Parts

For the construction of 1 smart rock you need one of each of these parts. Please be aware of the tolerence of these parts when printing them so they fit together.

Some Smart Rocks don't need the 3D printed rails. If given the oportunity we recommend switching to this verion for the convience and simplicity.

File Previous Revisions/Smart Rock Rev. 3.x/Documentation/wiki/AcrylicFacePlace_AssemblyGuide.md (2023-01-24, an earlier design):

# Acrylic Faceplate Assembly Guide

The Acrylic face plate houses both the OsmoPod and the Turbidity sensor for the Smart Rock.

**Materials**

* Acrylic Face plate
* Turbidity Sensor
* Osmopod

Additional Materials

* 30mL cup
* popsicle stick
* Marine Epoxy
* Super glue
* Scissors
* Paper Towels

**End Cap Assembly Procedure**

1. Prep the Turbidity sensor by using the scissors to trim the two mounting tabs off.

2. Cut the tip of the marine epoxy with the scissors - *be careful as it can ooze after opening*

3. Squeeze out 15 ml of marine epoxy into the 30 ml cup and mix thoroughly using a popsicle stick.

4. Apply marine epoxy around the flange edge of the turbidity sensor.

5. Insert the turbidity sensor into the large circular hole in the face plate. The black plastic peg should point directly at the oval slot on the face plate.

6. With the turbidity sensor in the face plate, apply super a small dab of epoxy to the outside of each arm on the sensor and apply the sensor cover. Apply pressure on the back of the sensor and the cover compressing it against the face plate. let it rest with the sensor cover facing down. 

7. Use the popsicle stick to move or add epoxy to turbidity sensor to create a good seal on the inside of the face plate if there are any holes or gaps.

8. Apply a small bead of epoxy around the lip of the osmopod cover facing outward. 

9. Apply a small drop of super glue on either side of the slot on the inside of the face plate. 

10. Align and insert the osmopod sensors so they clear the super glue and make a good seal against the face plate. Add more epoxy if there are any gaps or holes. The wires can stick straight up into the air while the epoxy dries. 

8. Set somewhere safe to dry for at least 4 hours to set, overnight to completely harden.

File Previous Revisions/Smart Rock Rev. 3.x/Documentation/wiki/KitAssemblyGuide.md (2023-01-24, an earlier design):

# Kit Assembly Guide

Welcome to the Kit Assembly Guide. Assembling the kit will take roughly one hour to complete from start to finish.

### Kit Contents

Hardware
- [ ] PVC Enclosure
- [ ] M3 Nut (10x)
- [ ] 8mm M3 Screw (2x)
- [ ] 10mm M3 Screw (4x)
- [ ] 3" Velcro Cable Tie

Laser Cut Parts
- [ ] Sled_Base
- [ ] Electronics_Mount
- [ ] Turbidity_Mount

3D Printed Parts
- [ ] Battery_Mount

Electronics
- [ ] Feather M0
- [ ] Hypnos
- [ ] EC Breakout Board
- [ ] 16GB Micro-SD Card
- [ ] Micro-SD Card to SD Card Adapter
- [ ] 3.3V 2200mAh Li-Po Battery
- [ ] Coin Cell Battery
- [ ] Li-Po Battery Charger
- [ ] Acrylic Faceplate

Additional Items
- [ ] Desiccant Packet (2x)

More information about parts and where to source them can be found in the [Bill of Materials](https://github.com/OPEnSLab-OSU/SmartRock/wiki/Bill-of-Materials).

### Electronics Information

Before you start assembling, open your lithium battery and get it on the charger. It will take a couple of hours to get it charged for the first time. Lithium-ion batteries pose a serious fire risk when charging or discharging. Please be mindful of charging location, any damage to a lithium ion battery can lead to fire. If a battery's casing starts to show signs of damage or if the battery gets puffy please **stop using the battery immediately** and recycle it responsibly. If you have more questions please refer to your batteries MDS and safety information.

Circuit boards should be conformal coated before being deployed underwater. The OPEnS Lab conformal coats all boards before shipping them for the longevity of the probes. Please **DO NOT Solder on a board that has been conformal coated** the fumes are extremely toxic. If boards are not conformal coated be mindful of touching the circuit boards without actively grounding your body. The static charge in your body may damage or ruin the components. If you need to solder please use the correct conformal coating removal gels before doing so and  

It is unlikely but possible when handling micro-SD Cards to damage or corrupt the data stored on the card. Try not to touch the pins (Gold pads) on the card, the static charge of your body can wreak havoc.

### Sled Assembly

**Materials**

* Sled_Base
* Electronics_Mount
* Turbidity_Mount
* Battery_Mount
* 8mm M3 Screws (2x)
* 10mm M3 Screws (4x)
* M3 Nuts (10x)
* Turbidity Breakout Board
* EC Breakout Board
* 3-pin JST Cable *(Male to Male)*
* 3" Cable Tie

Additional Materials

* pliers can be useful here

**Sled Assembly Procedure**

1. Lay out the Electronics_Mount with the sloped corners in the top left. Take two 10mm screws putting them up through the Electronics Mount in opposite corners and capturing each with 1 nut to make posts. 

2. Set the EC Breakout board on the posts of the Electronics_Mount with the JST Connects on the Right. Then capture it with another nut on each post. 

3. Lay out the Turbidity_Mount with the sloped corners in the top left corner. Take two 10mm screws and put them up through the Turbidity_Mount in opposite corners. Capture each of them with 1 nut to make posts. 

4. Set the Turbidity Breakout Board on the standoffs with the Blue Box on top and switch on bottom and capture it with two more nuts.

5. Take the 3" Velcro Cable tie and stick it to its self making a loop. Put this around the battery mount lining it up with the slot. 

6. Take the Electronics_Mount with the EC Breakout Board mounted and mesh it with the battery mount in the two slots on the prints side. Make sure the Velcro tie is sitting in the slot not interfering with the two parts touching. Take the Turbidity_Mount with the Turbidity Breakout board attached and slot it over both the Battery Mount onto the Electronics_Mount's tabs.

7. With the Mounts and print slotted together drop it into the Sled_Base using the Tabs and slots making sure the Velcro tie doesn't interfere.

8. Take two 8mm bolts and drop them through the Battery_Mount into the Sled_Base. Capture them with a nut on the bottom of the Sled_Base.

9. Plug the 3-pin JST into the Turbidity breakout board in the beige connector closer to the EC Breakout Board. Tuck the cable in by Wrap it in one loop and plug it in the the 3-pin JST plug on the EC Breakout Board.

<!-- 
![Turbidity_SledAssembly](https://github.com/OPEnSLab-OSU/SmartRock/blob/master/Previous%20Revisions/media/Sled_RailAssembly.gif)
-->

<!--
### Enclosure Assembly

**Materials**

* PVC Enclosure *(Assuming it is fully assembled and cemented in place)*
* Rail_Outside

Additional Materials

* Super Glue

**Enclosure Assembly Procedure**

1. Remove the cap on the PVC enclosure to get easy access to the inside lip of the housing. 

2. Identify the lip that is the end of the pipe and the start of the union fitting and find a clean spot to attach the rail to.

3. Use the Rail_Outside to do a test fit, if it the location looks good apply super glue to the curved bottom of the Rail_Outside *(be careful not to apply it to the retaining clip)*

4. Align the front edge of the Rail_Outside, the open side, with the front edge of the pipe and apply pressure until the super glue has set. *(Try and make it as straight as possible to make sliding the electronics as easy as possible.)*

5. Once the super glue has set use the sled to check that it is straight enough to go all the way in. The front edge of the two rails should be flush.
-->

### Electronics Assembly

**Materials**

* Feather M0
* Hypnos Board
* Micro-SD Card
* Coin Cell Battery
* Sled Assembly

** Electronics Assembly Procedure**

1. Insert the coin cell battery into the Appropriate slot on the Hypnos Board. The positive side of the battery faces outward from the board.

2. Plug the SD card into a computer and confirm that a config file is loaded.

3. With the config file confirmed plug the SD card into the Hypnos Board. The gold pins on the card face the PCB of the Hypnos.

4. Stack the Feather onto the Female headers on the Hypnos Board. Make sure the two are aligned and every pin is in a header, there should be no extra pins. 

5. Stack the Feather and Hypnos on to the EC Breakout Board on the Sled. Ensure once again there are no extra headers. 

6. Double check the stack of PCBs to ensure they are completely plugged in and secure. 

### Sensor Assembly

**Materials**

* Acrylic Faceplate With sensors 
* Turbidity Wire

**Sensor Assembly Procedure**

1. Inspect both ends of the Turbidity Wire and uncoil it slightly. Take the end with the clip and plug it into the **Turbidity sensor**, the remaining end will plug into the white connector on the Turbidity Breakout Board. This cable is directional please double check it is in correctly.

2. Plug in the 2-pin and the 4-pin wires from the OsmoPod to the EC Breakout Board 

## Conclusion

The sled should slide into the enclosure relatively easily. Center the acrylic faceplate and ensure it is resting flush before screwing on the top of the union fitting.

If you are interested in how the in "house parts" are built you can visit the In-House Parts section of the wiki to find their assembly guides.

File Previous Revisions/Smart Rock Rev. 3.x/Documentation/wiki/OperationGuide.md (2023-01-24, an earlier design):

# Operation Guide

Welcome to the Operation Guide. To start using your Smart Rock please charge the 3.3V Li-Po battery using the included charger.

On the bottom of the Hypnos board there is a holder for the coin cell battery to attach. The positive pole of the battery points away from the board and makes contact with the protruding metal housing. Next comes the SD card which is installed with the contacts facing the board. When the SD card is installed it should go in easily and click in place.

With the feather M0 installed on the Hypnos, plug the feather into a computer using the included micro-USB cable. The computer should have a serial monitor installed, we use the one that comes with the Arduino IDE. Have the serial monitor ready so when it boots up you can set the time on the clock, if you don't get to it before it goes to sleep/ starts taking data it should take the time from the computer it is plugged into and use that. You can power off the Smart Rock and check the SD card to make sure the correct time is stored on the SD card. To ensure the time is set, power on the Smart Rock using the 3.3V Li-Po battery and let it collect a data point or two and check the SD card to make sure the time is being kept correctly. 

If everything looks good, you are good to deploy your unit after validating/ calibrating the sensors to your liking.

## Troubleshooting

Your Smart Rock comes preprogrammed and includes software that is stable for long term use.
However, it is possible for unexpected behavior(s) to occur.

Below is a list of behaviors that may occur or have occurred, with detailed steps to solve them.

## [My Smart Rock is not turning on when I plug in the battery]

This behavior often occurs because the battery is not charged. To verify that the battery is the issue follow the steps below.

### Fix 1

	+ Check that the battery is charged
		- Plug battery into charging port
		- After the battery is charged, plug battery into Smart Rock power port
		- The Smart Rock should turn on and begin it's normal operation
		- If Smart Rock does not turn on and begin normal operation, proceed to next step

### Fix 2

	+ Plug the Smart Rock into a computer using the provided micro USB cable
		- The LEDs on the Smart Rock should turn on and proceed to it's normal operation. 
		- If the Smart Rock turns on and resumes operation while plugged into the

## [Why are the LEDs on my Smart Rock staying solid red; No blinking]

This behavior sometimes occurs for a number of unknown reasons, it could happen from handling the Smart Rock and accidentally moving one of the wires too much, or it could be caused by a poorly soldered pin that is causing a short. It may also be caused by a corrupted upload of the Arduino sketch.

### Fix 1

	+ Simply, restart the Smart Rock by pressing the Reset button on top of the Smart Rock electronics assembly.
	+ If the Smart Rock does not resume normal operation, proceed to Fix 2.
 
### Fix 2
	
	+ Unplug the battery from the Smart Rock
	+ Wait 10 seconds
	+ Plug the battery into the Smart Rock again
	+ If Smart Rock does not resume normal operation, proceed to Fix 3
### Fix 3 

	+ Unplug the battery from the Smart Rock
	+ Remove Smart Rock electronics assembly
	+ Disassemble Smart Rock electronics assembly
		- Remove the top black Arduino Feather board
		- Remove the middle green Hypnos board
	+ Examine each individual board for errors in solder points.
	+ If there are any noticeable errors in the soldering, proceed to correct these errors with the appropriate tools.
	+ If solder errors existed and have been corrected, reassemble Smart Rock electronics assembly
    + If issue persists, proceed to Fix 4

### Fix 4

    + Plug Smart Rock electronic assembly into computer

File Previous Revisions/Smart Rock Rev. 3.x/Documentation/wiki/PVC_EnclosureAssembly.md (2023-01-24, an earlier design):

# PVC Enclosure Assembly

The PCV Enclosure's construction is crucial to the strength and reliability of the Smart Rock. Every joint must be correctly welded with glue that has not expired and tested for a good seal. 

**Materials**

Item Description | Notes | Quantity per 1 SR | Part Number | Dist. Website 
------ | ------ | ------ | ------- | ------
PVC Pipe (length in inches) | 2.5" pipe diameter | 4.125 | 5AFJ8 | [Grainger](https://www.grainger.com/product/GRAINGER-APPROVED-Pipe-5AFJ8?)
PVC Union Fitting | Only part of the fitting is used, cemented onto pipe | 1 | 457-025 | [SupplyHouse](https://www.supplyhouse.com/Spears-457-025-2-1-2-PVC-Sch-40-Socket-Union-w-Buna-N-O-ring)
PVC Cap Fitting | Cemented onto pipe | 1 | 447-025 | [SupplyHouse](https://www.supplyhouse.com/Spears-447-025-2-1-2-PVC-Schedule-40-Cap)

**Additional Materials**

- [ ] PVC Primer
- [ ] PVC Welding Glue
- [ ] Paper Towels

More information about parts and where we source them can be found in the [Bill of Materials](https://github.com/OPEnSLab-OSU/SmartRock/wiki/Bill-of-Materials).

** Safety **
Please complete all PVC Enclosure Assembly in a well ventilated area. The glue used to weld the PVC gives off strong fumes. Please refer to the glue, and primer, MDS and instructions for specific safety procedure and information regarding use and storage.

1. Start by Preparing the union fitting for gluing. The screw cap, O-ring, and adapter need to be removed. The adapter will not be needed and can be discarded. To remove the O-ring pry on one edge with a blunt tool, work the ring out of the slot using the pry tool and you fingers. 

2. Using the Primer coat the fittings and the pipe, just where they will overlap. Let the primer sit for a minute and "dry" it will still be tacky to the touch however it will lose its shine.

3. Apply glue to the union fitting and with the pipe standing up push the union fitting down until it hits the hard stop. Do this quickly as the glue sets fast. Apply pressure to the fitting for about 60 seconds for the glue to set.

4. Apply glue to the cap fitting and with the pipe standing up push the cap fitting down until it hots the hard stop. Do this quickly as the glue sets fast. Apply pressure to the fitting for about 60 seconds for the glue to set. 

5. Re-install the o-ring to the grove of the union fitting, then screw on the cap.

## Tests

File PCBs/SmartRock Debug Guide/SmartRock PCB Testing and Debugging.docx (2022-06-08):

SmartRock PCB Testing and Debugging

Ohm/Voltage Meter

The most important tool used in making sure a board can be used is the voltage meter. Below is an image of one, the lab will have multiple and may look different.

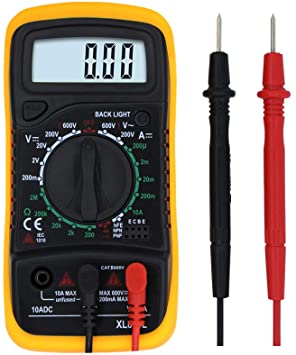
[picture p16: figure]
Amazon.com: LeeWoo Electrical Digital Multimeter, Handheld Data Hold Electronic Amp, Volt Current Ohm Voltage Meter for Transistor Test &amp; Diode Test, Support Backlight Screen: Automotive

This can be used to check voltages, currents, resistance, capacitance, inductance, diode bias direction, and importantly for our use signal connections. This signal connection tool will have an icon that will resemble an audio icon. Icon 12 on the following multimeter is the icon you want.

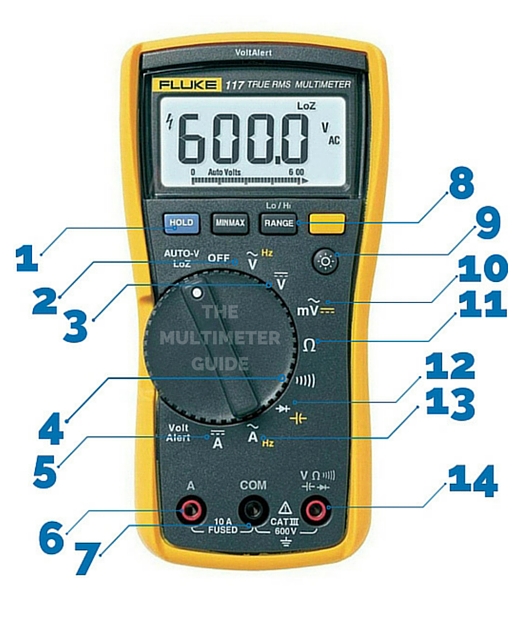
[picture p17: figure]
Multimeter Symbols – What Do They Mean? - The Multimeter Guide

Setting the dial to this setting will cause a noise to be emitted by the tool whenever the two leads (one ground and one high voltage) are touched together. This is useful as now that traces on the PCB can be checked before applying any power to the electronics. Other options on the multimeter dial are also useful and will want to be utilized depending on what needs to be checked or debugged.

First check over – before powering on

There are two very important things to double check before powering on a board, one may fry components if an issue is present. The other isn’t as vital but must be correct for board operation. These tests will use the trace short circuit tool in the multimeter explained above.

Power and Ground

Circled in the circuit are a few contacts for the power and ground of the PCB.

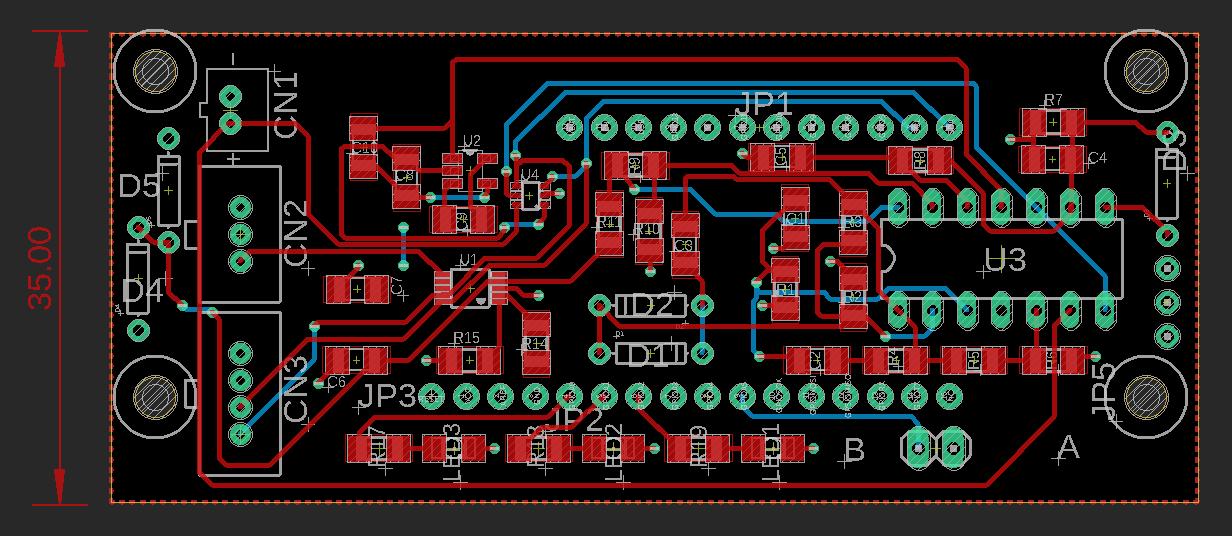
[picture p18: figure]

The red circles are the two points for the VCC plane and the light blue circles are the two points for the GND plane. To check that these are working correctly, first put one probe on a red circle and one probe on a light blue circle. If you here a tone from the meter that indicates that these are connected. This is a major issue and the board should NOT be powered on – power in this case could cause some high currents to be conducted shorting components or burning out the controllers. If no tone is made there are no issues here. If there is an issue look at any components that connect to both VCC and GND, something is causing a short in the soldering. Some culprits to check first would be U1, U2, U3, and U4 (the chips), and then the smaller components such as resistors and capacitors as well as the microcontroller headers.

The second test is to put probes on both red and then probes on both light blue. Each one of these tests should have a tone and means the board doesn’t have any major defects in the power planes and all components will most likely be powered correctly. If there is no tone there was a problem in manufacturing. This is fixable but is difficult and unreliable as a product, a new board should just be constructed and used instead.

I2C Lines

Everything in this board utilizes I2C for sensor communication, so making sure these are correctly operating is a useful check. This is good to do before power on but can be done later. Generally, if the code cannot see/sense a sensor that it is supposed to something is wrong with the I2C trace and this check can be done to localize the problem area. The following board diagram will show the points that are connected to the two I2C lines.

The yellowish colored shapes show where the SDA connections and the white shapes show the SCL connections. The checks to make here are similar to the VCC and GND checks made earlier. First probe multiple spots of the yellow circle to make sure they are all connected, then do the same for the white spots. A tone should be made when both probes are on the same color. Then place one probe on each color, if a tone is made that means a short is being made in the solder somewhere. This is a little tricky to track down as there are multiple places this short could be, visual inspection with a microscope will be useful in this instance. Resoldering or taking an exacto knife or razor to the shorted solder may be enough to fix the issue.

Second Test – Power

Now that the important traces are checked the board can be powered on as if it were to be used. Apply the entire stack, i.e. with the hypnos and feather, making sure to supply voltage through the hypnos. Then using the multimeter set the settings to voltage and probe the earlier mentioned VCC and GND (the red and blue circles respectively). There should be a voltage of about 3.3V showing up on the multimeter. The second test is the supply voltage for the EC sensing circuit. Probe the two spots shown below.

The yellow and the white circles are the supply points for the EC circuit. Using the same voltage mode on the multimeter place one probe on each spot, the readout should be either 6.6V or -6.6V. A negative is fine here, it just depends which probe is placed where. The true voltages on these spots are 3.3V and -3.3V volt, but the meter will show them together as a 6.6V. If this is not what is shown then the negative voltage supply has an issue, this is the U2 chip. Check the solder here and make sure all of the surrounding circuitry is soldered correctly.

These are the main checks – other issues will need more detailed and specific debugging. The steps detailed in this document will get the board quickly checked and off the ground for more rigorous testing with code. The next test I would do it connect a feather with an I2C address scanner script to make sure all of the I2C devices are shown – if more info is needed for this step reach out to Cameron Whitlow on basecamp. For other niche debugging questions feel free to reach out as well.

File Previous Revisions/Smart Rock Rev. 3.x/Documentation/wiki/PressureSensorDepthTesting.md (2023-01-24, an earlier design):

# Pressure Sensor Depth Testing

Performed and documented by Kaden Bennett and Chris Milford

**Experiment Description**

A Smart Rock was deployed overnight at the bottom of a 4 meter standpipe, using a nylon rope tied around the PVC casing for deployment and retrieval. Attached to the Smart Rock was a HOBO pressure and temperature logger (hereafter referred to as the &ldquo;silver HOBO logger&rdquo;). This logger was attached to the Smart Rock with stainless steel hose clamps and zip ties. The experimental setup can be seen in the Deployment Information section below.

Outside of the standpipe, there was deployed a second HOBO pressure and temperature logger (hereafter referred to as the atmospheric HOBO logger). This logger measured the atmospheric pressure in the vicinity of the standpipe, for use in pressure compensation. In order to calculate the depth of both the Smart Rock and the silver HOBO logger, the absolute pressure readings were both adjusted by subtracting the atmospheric pressure present outside the standpipe at that moment in time, as recorded by the atmospheric pressure logger.

**Deployment Information**

Time (PDT) | Event | Data Collected
-- | -- | --
8/25/22 5:09 PM | Smart Rock submerged at full testing depth | Stage height: 399 cm
8/26/22 10:37 AM | Smart Rock retrieved from standpipe | Stage height: 398 cm

###### Table 1: Deployment Timeline

There was a 5 cm offset between the Smart Rock and silver HOBO logger pressure sensors in our experimental setup, as can be seen below.





</span></span></p><p dir="ltr" style="line-height:1.3800000000000001;text-align: center;margin-top:0pt;margin-bottom:0pt;">

###### Images 1-2: Experimental Setup of Smart Rock and Silver HOBO Logger

* The Smart Rock was sealed by the normal process, with a set screw and vacuum grease, which has been shown to consistently prevent leakages in previous deployments. However, upon retrieval, it was observed that water had infiltrated the internal Smart Rock compartment. This may be a result of the higher pressures endured during this experiment in comparison with our typical shallow water deployments and tests.

**Pressure Data:**



###### Figure 1: Smart Rock and HOBO Logger Absolute Pressure Data



###### Figure 2: Smart Rock and Silver HOBO Logger Depths</span></p><br /><br /><p dir="ltr" style="line-height:1.3800000000000001;margin-top:0pt;margin-bottom:0pt;">



###### Figure 3: Atmospheric HOBO Logger Pressure Data

* The stair-step behaviour observed in the first few hours of the depth data (prior to 5:09 PM) is a result of the gradual filling of the standpipe and the plugging of various leaks which arose during the deployment.

* In the calculation of the depth of the Silver HOBO logger, it was taken into account that there was also a 0.62 mbar reading differential between that logger and the HOBO logger used to measure atmospheric pressure. This value was calculated as the average difference between the atmospheric pressure readings of the two loggers before the deployment began. The Smart Rock had a reading differential of less than 0.01 mbar with the atmospheric pressure logger, so that value was treated as insignificant.

* A constant conversion factor of 1.01972 was used to convert from mbar pressure units to cm of water head.

* The observed difference between the recorded depths of the Smart Rock and the silver HOBO logger is partially due to a 5 cm offset in the sensor height in our experimental setup.

* The calculated error of the Smart Rock pressure sensor at a submerged depth of ~4m is 3.45 mbar / 3.52 cm, after accounting for the sensor offset.

* A comparison of this data along with the result of our previous standpipe test against the data sheet specifications of the MS5803 pressure sensor used in the Smart Rock is shown below. As can be clearly seen, the performance of the Smart Rock&rsquo;s pressure sensor deteriorates quicker with increasing pressure than the manufacturer's specifications would suggest. This is likely a result of other temperature/pressure dependent components of the Smart Rock electronics.



###### Figure 4: Pressure Error Comparison with Manufacturer Specifications

* Ultimately, this error is still less than 0.5%, considering the magnitude of the absolute pressure reading. When compared to the water depth being analyzed, the error is slightly below 1% of the water pressure reading. This offset of 3-4 cm at a water depth of around 400 cm is not hugely significant, but is worth keeping under consideration for deep water Smart Rock deployments.

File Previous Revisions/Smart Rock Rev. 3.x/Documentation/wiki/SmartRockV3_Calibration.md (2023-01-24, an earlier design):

# Smart Rock V3 Calibration

To calibrate the Smart Rock V3 and its revisions please use the CUAHSI 2021 Materials. The calibration guide can be found [here](https://github.com/OPEnSLab-OSU/SmartRock/blob/master/Workshop%20Materials/CUAHSI%202021/SmartRock_AssemblyGuide_CUAHSI_2021.pdf) and the spreadsheet templates you will need can be found in the CUAHSI 2021 workshop materials [here](https://github.com/OPEnSLab-OSU/SmartRock/tree/master/Workshop%20Materials/CUAHSI%202021).

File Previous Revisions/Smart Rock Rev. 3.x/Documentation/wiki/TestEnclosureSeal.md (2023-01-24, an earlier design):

# Test Enclosure Seal

Testing for leaks in the enclosure is pretty straight forward.

**Materials**

* Enclosure
* Acrylic Faceplate

Additional Materials

* Silicone Grease
* Tub of water

1. Start by removing the sled if it is installed in the smart rock.

2. Clean the O-ring of any dust or debris then add silicone grease to the to help create a water tight seal.

2. Put on the acrylic face plate and seal union fitting. The Smart Rock should not have any electronics inside in case there is a leak. The o-ring should be visibly compressed against the acrylic.   

3. Completely submerge the Smart Rock in water and hold it there for 30 seconds.

4. Remove the Smart Rock and check for leaks by looking for water pooling inside the Smart Rock. If there are none re-submerge for 3 to 5 minutes.

5. Check for water pooling inside the Smart Rock, if none can be seen then it is ready to be opened. 

6. Unscrew the union fitting and fell for water inside. If there is no water inside the smart rock it is not leaking.

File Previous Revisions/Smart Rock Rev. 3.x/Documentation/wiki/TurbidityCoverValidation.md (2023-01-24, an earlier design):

# Turbidity Cover Validation

To validate the turbidity cover as effective it will have to show that it is effective at...

* Protecting the Turbidity sensor and keep it from getting pushed into the Smart Rock.
* Blocking stray light from interfering with the turbidity sensor.
* Not affect its ability to take measurements. 

To verify the effectiveness of the cover at this it will undergo a mechanical review to show how its geometry will prevent the sensor from caving in. To verify that the sensor cover blocks light two experiments will be conducted. The first will show the effectiveness of of the cover to block light by showing readings with and without the cover in different positions. The second will test how the much the cover affects the turbidity reading by testing known solutions with the sensor covered and uncovered.

**Mechanical Review**

The Turbidity cover is meant to use the sides of the sensor as a guide to hold it in position as it covers the top and sides completely. It is not meant to touch the top of the turbidity sensor, leaving a small gap between the cover and the sensor. The base of the turbidity cover has a flange which sits against the acrylic face plate transferring any force pushing on the turbidity cover into the acrylic face plate. This prevents the sensor from getting pushed into the Smart Rock flooding the unit. Below are two animations made using the CAD of the Smart Rock, one showing the the system with a cover and the other without. This shows that without a cover if enough force is applied it can break the epoxy sealing the sensor to the face plate creating a leak or completely flooding the unit.   

###### _Figure 1. Turbidity Sensor with cover_
TurbidityCover_Cross

###### _Figure 2. Turbidity Sensor without cover_
Tubridity_Exposed

**Turbidity Cover Validation**

For the turbidity cover to pass the validation it must block stray light from influencing the sensor without interfering with the sensors abilities to collect data. First the sensor will be tested to see what wavelengths of light it is actually reading so when I preform my tests I know that my light source will have a measurable impact on the sensor. Then I will run tests to ensure that the cover actually blocks stray light from interfering with the sensor. After it's confirmed to block light it will be tested to see how it affects the sensors ability to collect data. All the following data is the raw analog values that the sensor stores. Because of this when light interferes with the sensor an increase in analog output should occur. This is because the sensor is made of a LED and a diode, the value recorded is the amount of light that can pass across the gap between the emitter and receiver. This translates to cleaner water lets more light pass, resulting in a higher value. 

For the first test different light sources were shine into the sensor directly. This tells us what frequencies of light actually are being measured by the sensors receiver by how large of a jump they cause. As seen in figure 3 the light on the blue end of the spectrum going into the ultra-violet had the largest response while the infrared was barely picked up. 

###### _Figure 3. How effective different sources of light influence the sensors readings._
Turbidity_Light_Influence

Moving forward the white LED is used for testing because it is the best balance of influencing the sensor and not too many high energy particles for safety during tests. This next test the Smart Rock took a measurement every second while the light was turned on and off every ten minutes. Half way through the test the turbidity cover was added and the intervals continued on and off every ten minutes. 

###### _Figure 4. Before and after having the cover on the sensor with stray light._
Turbidity_Cover_Blocking

This shows that the turbidity cover does effectively lower the stray light interfering with the sensor. The light interference on the sensor is reduced by %80 by adding the turbidity cover as seen in figure 4. The cover definitely blocks interfering light and to test if it will interfere with the sensors measurements I filled a tub with filtered water. I also measured 500mL of warm filtered water into a glass and mixed it with two Nescafe Taster's Choice instant coffee packets, each meant for 8oz. Stirring until the instant coffee was dissolved and then let to sit for 5 minutes before being stirred again to ensure all the crystals had fully dissolved. 100mL of instant coffee was added at a time and sat until it had completely dispersed into the tub evenly. Then another 100mL was added until there was no more. This was done for the Smart Rock with and without a turbidity cover cleaning everything thoroughly between tests.

###### _Figure 5. Turbidity reading with and without the cover._
Turbidity_Cover_Interference

The raw data was adjusted to align the start times of the two trials to make comparing easier. When the instant coffee is initially added both variations spike to roughly the same value however the sensor without a cover has a harder following the steady increase in turbidity. At the end of both trials the sensors are taken out of the coffee tub, washed to remove any coffee from the outside, then put into another tub of clean water to get another base line. While the sensor with a cover returns to roughly the same initial value the sensor without a cover struggles to recover to its initial value. I think this may have been due to some other factor as I would expect the sensor to increase more than it did even though it did become stable. 

<!--
![Turbidity_Side](https://user-images.githubusercontent.com/22950096/108502963-7c269280-7268-11eb-88b0-6957515014e3.png)
--!>

To conclude the turbidity cover succeeds at its goal both mechanically protecting the sensor and blocking stray light from interfering with its readings. The cover is validated to be implemented on the Smart Rock. The turbidity cover can also be applied to previous versions of the Smart Rock to improve their measurements and protect them from leaks and damage as well.

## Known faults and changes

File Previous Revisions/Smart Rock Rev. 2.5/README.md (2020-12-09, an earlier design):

# Smart Rock | [Updates](https://github.com/OPEnSLab-OSU/OPEnS-Lab-Home/wiki/smart-rock-updates) | [Github](https://github.com/OPEnSLab-OSU/SmartRock)
Project Leads: **Alicia Veach**, **Martin Escoto**, and **Colin Hale-Brown**

Interest in the project? Email us at: halebroc@oregonstate.edu

## Overview
Current hydrological modelling is missing data from small and seasonal streams. Data collection on these streams is sparse with measurements, if any data is taken at all. Small streams are often ignored in hydrological modelling by entities that generate public data of water resources. The ecological health of habitats for fish depends on the flow of these small streams during different seasons. monitoring can be expensive and exclusive to organizations that can afford to do so. Current barriers prevent current hydrological modeling being informed by small and seasonal streams. 

Smart Rock aims to create a low-cost device to monitor remote streams through citizen science. The device could be used as a learning tool for students, teachers, and other citizen scientists. Deploying Smart Rock in streams will allow for more accurate data collection of small and seasonal streams.

Cover<!--- {{:20190427_164150.jpg?400|}} -->
## Description

The Smart Rock is a submersible sensor suite that monitors water depth, temperature, turbidity, and salinity (EC) of a small stream over time and designed to be built by anyone with or without extensive experience in electronics.
Current capabilities of Smart Rock sensors are depth measurement with accuracy within 0.13 mbar resolution as compared to an out of water pressure sensor, temperature accuracy of fewer than 0.01°C, turbidity measured in JTU, and a salinity measurement that increases accuracy to less than 5 parts per million. Battery life for Smart Rock is up to 3 months with low power sleep, a function that limits power usage from the device when dormant. This can be extended by taking data less often than once every 20 minutes. The device currently costs ~ $200 with these specifications and custom parts and takes about 10 hours to assemble and program.

**Adafruit Feather M0 Basic Proto**

<details>
<summary>Show More</summary>

General Description/how it works:
	The Feather M0 Basic Proto is an Arduino-compatible microcontroller that runs on 3.3 volts. A 3.3 volt regulator allows for a 3.7 volt lithium polymer battery to be used. The feather has a 500mA peak current, has 20 GPIO pins, 10 analog inputs, and 1 analog output. These pins allow users to connect their sensors and motors to the controller to program readability and functions with Arduino.

Smart Rock Use Validation:
	The Feather M0 Basic Proto acts as the main microcontroller for Smart Rock. Integrated into the PCB, the feather gives inputs to sensors and other electronics and reads outputs. Sensors operate on the I2C interface and analog inputs. The Feather saves data to SD in a spreadsheet from the stream on Hypnos.
</details>

**Pressure/Temperature Sensor**

<details>
<summary>Show More</summary>

General Description/how it works: 
The pressure sensor runs on 3 volts from a microcontroller or direct source. The MS5803 Pressure sensor uses piezoresistivity to output pressure readings. Piezoresistivity is the change in electrical resistivity of a semiconductor when mechanical strain is applied. The sensor converts an analog output into a 24 digit output that runs on the I2C protocol. The sensor additionally provides a 24 digit output for temperature. The sensor has been calibrated at 2 temperatures and 2 pressures and 6 coefficients are calculated and stored in a 128-bit PROM. When taking new readings, the device first reads this calibration data. The digital pressure data (D1) and digital temperature data (D2) are read and temperature and pressure are then calculated. Temperature is calculated in two steps: subtracting the read temperature from the reference temperature and comparing to the temperature coefficient from calibration. Then, the electrical sensitivity is read and the actual temperature calculation is used in another calculation regarding the pressure offset caused by temperature. Following I2C protocol communication, SDA (Serial Data) output conveys the pressure and temperature readings to a microcontroller.

Smart Rock Use Validation:
	The pressure and temperature gives a two for one. Costing $10.72, this sensor provides the two primary measurements we need with one sensor. Measuring temperature and depth of a stream are the most useful in determining basic data about a remote and unknown stream. With a custom PCB designed for this sensor, connecting the sensor to the microcontroller is made easier. Following I2C protocol, the sensor is already implemented into LOOM_Library. This allows for the programming of the system to be simple. The sensor gives accurate and useful data within our budget. The size of the sensor is also fairly small and easy to make water proof.

pressure

</details>

**Turbidity Sensor**

<details>
<summary>Show More</summary>

General Description/ How it works:
	Turbidity is the measurement of the cloudiness in a liquid. This sensor uses a measurement of light transmittance to determined the total suspended solids (TSS) in the liquid. TSS increases with turbidity. Turbidity is measured in JTU which can be used to determine the cleanliness of the water, water erosion, and pollution. The sensor gives an analog output that can be converted to a measurement in JTU. Using a laser signal between two nodes, the device can convert cloudiness to JTU.

Smart Rock Use Validation:
	Turbidity in a stream can indicate the overall quality of the water and gives an idea for the amount of erosion occurring. Adding this sensor to the Smart Rock is both cheap and simple. The sensor from DF Robot costs $9.90, making it easy to keep Smart Rock inexpensive. The sensor can be hooked up to the Smart Rock through three easy connections, 3V power, GND, and an analog port. Implementing the sensor board to the electronics is relatively simple because it comes with a PCB that can be wired to the Smart Rock base PCB.

Turbidity

</details>

**Salinity Sensor**

<details>
<summary>Show More</summary>

General Description/How it works:
	TDS measures the amount of organic and inorganic dissolved solids in the liquid. Using electrical conductivity, the sensor gives an analog reading that corresponds to the amount of minerals in the water. The sensor has two probes and the interference between them changes the voltage and an analog reading can be taken. The sensor kit comes with its own PCB, the electrical conductivity probe, and the required connectors.

Smart Rock Use Validation:
	Having a salinity measurement on the Smart Rock is cost effective and important to proving the capability of the sensor package. Electrical conductivity gives an idea to the amount of salts and minerals in the stream and can be used to determine the overall health of the stream. With this sensor costing $12.90, much less than similar probes, the price of having this on the Smart Rock is low enough to implement. The size of the probe is fairly small and can be sealed to be waterproof easily.
</details>

**OPEnS Lab Hypnos**

<details>
<summary>Show More</summary>

General Description/ How it works:
	The Hypnos board is an attachable precision I2C integrated real time clock and data logger. A crystal is used to keep time and is temperature compensated inside the chip. A coin cell battery is plugged into the board to keep time even when the a feather battery is not connected. Data can be saved and read from SPI or I2C protocol communication.

Smart Rock Use Validation:
	The Smart Rock is using the Hypnos to keep temperature compensated time as well as storing all the data read by the sensors while in the stream bed. Smart Rock takes data every 10 minutes and this device allows such to happen. The RTC sends a square wave signal to a digital pin on the feather to wake the device from the power sleep to take data. Having this RTC allows for the device to keep time even in a low-power sleep mode.

More information about the Hypnos Board can be found [here](https://github.com/OPEnSLab-OSU/OPEnS-Lab-Home/wiki/Hypnos).
</details>

<!--
**Reed Switch**

<details>
<summary>Show More</summary>

General Description/ How it works:
	A reed switch is a small device that closes/open when interacting with a magnetic field. It can be used for keeping a device off until opened, for example, a laptop screen. Always open reed switches remain open until a magnet is nearby. Then, it closes and allows current to flow through as a closed wire. Inside the switch there are two wires that are separated and held within a plastic frame. When a magnet is near, the two wire touch and allow current to flow.

Smart Rock Use Validation:
	The always open Reed switch for the Smart Rock is used as an interrupt. The device remains asleep until a user interacts with it with a magnet. The device can then wake and collect data to be transferred. The reed switch allows the battery to be saved by keeping the device off until it is used to collect and transfer data. The switch costs $1.08 for one, cheap and easy to implement. With LOOM, an interrupt can be easily added to wake the device when current flows from the ground to a desired pin, when the reed switch is closed.
</details>

**pH Sensor**

<details>
<summary>Show More</summary>

General Description/ How it works:
 pH is the measurement of hydrogen in a solution. This indicates the acidity of the water which is useful for the biological systems impacted by the stream. This pH sensor uses a pH composite electrode that gives a reading in millivolts that can be converted directly to pH using an analog reading. When calibrated, this probe has accuracy of +_ 0.1pH. 

Smart Rock Use Validation: 
This pH probe from DF robot comes with a pcb and the probe in standard solution. Although this probe is a lab grade probe and not meant for long-term submersion, this probe costs $29.50 and can give a good short term estimate of stream pH. Other probes tend to cost much more and are too bulky for the Smart Rock application. Having an estimate of pH can give information about the biological health of a stream. This pH sensor is also implemented into LOOM.

![ph](https://user-images.githubusercontent.com/55994278/68499450-1ac2e780-020e-11ea-8a1e-4b88694d1a3e.png)

</details>
-->

### Casing Design

The **outer Case** is made of a piece of PVC with union fittings attached to either end. The union fittings are mounted to the PVC using a layer of primer, then a layer of PVC cement. The smaller diameter, unthreaded, section of the union fitting is discarded and replaced with a circular piece of acrylic. This piece of acrylic has laser-cut holes for the sensors to be epoxied to make water-tight. The o-ring in the union fitting is coated in silicone grease to ensure a waterproof seal when the end of the union fitting is screwed back on with the acrylic. This modded union fitting design is used so that the electronics may be accessed and so that we can have the sensors protruding from one end without getting their wires twisted and tangled when the end is removed. 


_*Note that the image above does not include full electronics or official electronics layout._

The **internal Structure** is made up of a 3D printed rail and an acrylic platform. One section of the rail is glued to the inside of the PVC, the other section is glued to a length of acrylic. The electronics are then mounted using velcro to this acrylic and slide into the case using the rail system. Using the rail and acrylic slide makes it easy to remove/access the electronics and holds everything in place. The electronics stack up on the slide allowing for a compact design


_*Note that the image above does not include full electronics or official electronics layout._

## Objectives

### Overall Targets:

*  Low cost

*  Durable

### Electrical Function Targets:
<details>
<summary>Show More</summary>

*  Senses underwater pressure for depth

*  Senses stream temperature

*  Senses turbidity

*  Senses salinity

*  Battery life of at least 1 week

*  Clean and user-friendly electronics packaging

*  Keeps time for data collections

*  Connects to user easily
</details>

### Casing Function Targets:
<details>
<summary>Show More</summary>

*  Waterproof

*  Remains in the location of placement

*  Electronics are securely mounted

*  Simple design

*  Aesthetically pleasing

*  Safe for the environment

*  Withstand freezing temperatures

*  Easy internal access

*  Easy to retrieve and transport
</details>

## Outcomes

Current capabilities of Smart Rock sensors are depth measurement with accuracy within 0.13 mbar resolution as compared to an out of water pressure sensor, temperature accuracy of fewer than 0.01°C, turbidity measured in JTU, and a salinity measurement with an accuracy of less than 5 parts per million. Future developments will have <!--pH sensing and--> flow sensing from the use of multiple high-accuracy pressure sensors. Battery life for Smart Rock is up to 3 months with low power sleep, a function that limits power usage from the device when dormant. This can be extended by taking data less often than once every 20 minutes. The device currently costs ~ $200 with these specifications and custom parts and takes about 10 hours to assemble and program.

### Field Test January 2020
FieldTestphoto
Turbidityresults
TDSResults
BatteryResults

## Future

Updating the Smart Rock to improve reliability and ease of use. Simplifying electronics so that the salinity sensor board is built into the main feather breakout and replacing all the dupont wires and standardizing to JST connectors to make assembly straightforward and user-friendly.
 
Preparing for CUAHSI workshop in summer 2020.

## Resource List

The Bill of Materials for the current iteration of the Smart Rock can be found [here](https://github.com/OPEnSLab-OSU/SmartRock/blob/master/Smart%20Rock%20Rev%202.5%20Bill%20of%20Materials%20for%20GitHub.xlsx).

Link to Github page with code and PCB design files can be found [here](https://github.com/OPEnSLab-OSU/SmartRock).

### Tutorials

Here are Resources from the 2019 CUAHSI workshop can be found [here](https://github.com/OPEnSLab-OSU/SmartRock/tree/master/Workshop%20Materials)

## Key Words
OPEnS, SmartRock, Smart Rock, Feather M0, Adalogger, Arduino, Stream, Water Monitor, Hydrological Data, Hydrological Monitoring, Pressure, Temperature, Electrical Conductivity, Dissolved Solids, Turbidity, pH, seasonal streams, small streams

## References

Software

*  Fusion 360. (2018). San Rafael, California: Autodesk.

*  EAGLE CAD. (2018). San Rafael, California: Autodesk.

*  Arduino IDE. (2020). Turin, Italy: Arduino

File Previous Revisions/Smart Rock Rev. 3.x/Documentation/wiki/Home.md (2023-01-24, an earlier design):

# Home

<p align="center">
    </a>
<p>

Project Leads: **Colin Hale-Brown**, **Brenda Fasse**

<!-- Past team members **Annika Sundstorm** -->

Interested in the project? Email us at: halebroc@oregonstate.edu

<!--**We are taking pre-orders for the V3 Smart Rock at the form [HERE](https://forms.gle/heTsUhmxyKFWzNU9A).**-->
<!--
**Smart Rock Virtual Workshop with CUAHSI**: [Open Hydrological Sensor Technologies: DIY Stream Sensor Networks](https://www.cuahsi.org/education/training/training-and-workshops/open-hydrological-sensor-technologies-diy-stream-sensor-networks):
Monday September 20 - Wednesday September 22, 9:00 am PT  - 12:00 pm PT. [**Register**](https://web.cvent.com/event/a9b4330e-efd9-4988-a294-09152a079004/summary) by August 30 at 11:59 PM ET.
-->
_To return to the OPEnS Lab wiki click [HERE](https://github.com/OPEnSLab-OSU/SmartRock)._

## Overview
Current hydrological modelling is missing data from small and seasonal streams. Data collection on these streams is sparse with measurements, if any data is taken at all. Small streams are often ignored in hydrological modelling by entities that generate public data of water resources. The ecological health of habitats for fish depends on the flow of these small streams during different seasons. monitoring can be expensive and exclusive to organizations that can afford to do so. Current barriers prevent current hydrological modeling being informed by small and seasonal streams. 

Smart Rock aims to create a low-cost device to monitor remote streams through the ideals and goals of citizen science. The device could be used as a learning tool for students, teachers, and other citizen scientists. Deploying Smart Rock in streams will allow for more accurate data collection of small and seasonal streams.

Cover
<!--- https://user-images.githubusercontent.com/22950096/106802651-160b0000-6618-11eb-814b-6e9be7e951d1.jpg, https://user-images.githubusercontent.com/22950096/103161041-477aeb00-4791-11eb-861f-7c8f8370842b.jpg, 98612647-70125880-22a9-11eb-8660-03565f0426d8.png -->

## Description

The Smart Rock is a submersible sensor suite that monitors water depth, temperature, turbidity, and salinity (EC) of a small stream over time and designed to be built by anyone with or without extensive experience in electronics.<!-- Current capabilities of Smart Rock sensors are depth measurement with accuracy within 0.13 mbar resolution as compared to an out of water pressure sensor, temperature accuracy of fewer than 0.01°C, turbidity measured in JTU, and a salinity measurement that increases accuracy to less than 5 parts per million. Battery life for Smart Rock is up to 3 months with low power sleep, a function that limits power usage from the device when dormant. This can be extended by taking data less often than once every 20 minutes.--> The device currently costs ~ $250 with these specifications and custom parts and takes about 10 hours to assemble and program.

<!--
| Specification  | Metric | Value| SR Version | Date |
| ------------- | ------------- | ------------- | ------------- | -------------
| Battery life	| Months  | In Testing | 3 |
| Electrical conductivity | µs | In Testing | 3 |
| MS5803 Pressure | mbar | In Testing | 3 |
| MS5803 Temperature | °C | In Testing | 3 | 
| Turbidity | JTU | In Testing | 3 |
-->

### Device Components Info

<details>
<summary>Adafruit Feather M0 Basic Proto</summary>

General Description/how it works:
	The Feather M0 Basic Proto is an Arduino-compatible microcontroller that runs on 3.3 volts. A 3.3 volt regulator allows for a 3.7 volt lithium polymer battery to be used. The feather has a 500mA peak current, has 20 GPIO pins, 10 analog inputs, and 1 analog output. These pins allow users to connect their sensors and motors to the controller to program readability and functions with Arduino.

Smart Rock Use Validation:
	The Feather M0 Basic Proto acts as the main microcontroller for Smart Rock. Integrated into the electronics stack, the feather gives inputs to sensors and other electronics and reads outputs. Sensors operate on the I2C interface and analog inputs. The Feather saves data to SD in a spreadsheet from the stream on Hypnos.
</details>

<details>
<summary>Pressure/Temperature Sensor</summary>

General Description/how it works: 
The pressure sensor runs on 3 volts from a microcontroller or direct source. The MS5803 Pressure sensor uses piezoresistivity to output pressure readings. Piezoresistivity is the change in electrical resistivity of a semiconductor when mechanical strain is applied. The sensor converts an analog output into a 24 digit output that runs on the I2C protocol. The sensor additionally provides a 24 digit output for temperature. The sensor has been calibrated at 2 temperatures and 2 pressures and 6 coefficients are calculated and stored in a 128-bit PROM. When taking new readings, the device first reads this calibration data. The digital pressure data (D1) and digital temperature data (D2) are read and temperature and pressure are then calculated. Temperature is calculated in two steps: subtracting the read temperature from the reference temperature and comparing to the temperature coefficient from calibration. Then, the electrical sensitivity is read and the actual temperature calculation is used in another calculation regarding the pressure offset caused by temperature. Following I2C protocol communication, SDA (Serial Data) output conveys the pressure and temperature readings to a microcontroller.

pressure

MS580302BA Water Level Spec
| Pressure | Condition | Min | Max | Unit |
| -------- | --------- | --- | --- | ---- |
| Operating Range | Full Accuracy | 300 | 1100 | mbar |
| Extended Range | Linear Range | 10 | 2000 | mbar |
| Absolute Accuracy | at 25°C |  |  |  mbar |
| Absolute Accuracy | at 25°C |  |  |  mbar |
| Absolute Accuracy | at 25°C |  |  |  mbar |
| Absolute Accuracy | at 25°C |  |  |  mbar |
| Maximum Error | VDD=1.8V...3.6V | -2.5 | +2.5 | mbar |
| Stability |  | -1 | +1 | mbar/yr |

MS580302BA Water Temperature Spec
| Temperature | Condition | Min | Max | Unit |
| ----------- | --------- | --- | --- | ---- |
| Range |  | -40 | +85 | °C |
| Absolute Accuracy | at 25°C | -0.8 | +0.8 | °C |
| Absolute Accuracy | -20...85°C | -2.0 | +2.0 | °C |
| Absolute Accuracy | -40...85°C | -4.0 | +4.0 | °C |
| Maximum Error | VDD=1.8V...3.6V |-0.5 | +0.5 | °C |

The data above is from the data sheet provided by the manufacturer, a complete data sheet for the sensor can be found [here](https://www.te.com/commerce/DocumentDelivery/DDEController?Action=showdoc&DocId=Data+Sheet%7FMS5803-02BA%7FB3%7Fpdf%7FEnglish%7FENG_DS_MS5803-02BA_B3.pdf%7FCAT-BLPS0010) if you are interested in more details.

Smart Rock Use Validation:
	The pressure and temperature gives a two for one. Costing $10.72, this sensor provides the two primary measurements we need with one sensor. Measuring temperature and depth of a stream are the most useful in determining basic data about a remote and unknown stream. With a custom PCB designed for this sensor, connecting the sensor to the microcontroller is made easier. Following I2C protocol, the sensor is already implemented into LOOM_Library. This allows for the programming of the system to be simple. The sensor gives accurate and useful data within our budget. The size of the sensor is also fairly small and easy to make water proof.

</details>

<details>
<summary>Turbidity Sensor</summary>

General Description/ How it works:
	Turbidity is the measurement of the cloudiness in a liquid. This sensor uses a measurement of light transmittance to determined the total suspended solids (TSS) in the liquid. TSS increases with turbidity. Turbidity is measured in JTU which can be used to determine the cleanliness of the water, water erosion, and pollution. The sensor gives an analog output that can be converted to a measurement in JTU. Using a laser signal between two nodes, the device can convert cloudiness to JTU.

Smart Rock Use Validation:
	Turbidity in a stream can indicate the overall quality of the water and gives an idea for the amount of erosion occurring. Adding this sensor to the Smart Rock is both cheap and simple. The sensor from DF Robot costs $9.90, making it easy to keep Smart Rock inexpensive. The sensor can be hooked up to the Smart Rock through three easy connections, 3V power, GND, and an analog port. Implementing the sensor board to the electronics is relatively simple because it comes with a PCB that can be wired to the Smart Rock EC Breakout Board.

Turbidity

</details>

<details>
<summary>Salinity Sensor</summary>

General Description/How it works:
	TDS measures the amount of organic and inorganic dissolved solids in the liquid. Using electrical conductivity, the sensor gives an analog reading that corresponds to the amount of minerals in the water. The sensor has two probes and the interference between them changes the voltage and an analog reading can be taken. The sensor is built into the same board as the MS5803 and connects to the EC Breakout Board on the electronics stack.

Smart Rock Use Validation:
	Having a salinity measurement on the Smart Rock is cost effective and important to proving the capability of the sensor package. Electrical conductivity gives an idea to the amount of salts and minerals in the stream and can be used to determine the overall health of the stream. With this sensor costing ~$15.00, much less than similar probes, the price of having this on the Smart Rock is low enough to implement. The size of the probe is small and can be sealed to be waterproof easily.
</details>

<details>
<summary>OPEnS Lab Hypnos</summary>

General Description/ How it works:
	The Hypnos board is an attachable precision I2C integrated real time clock and data logger. A crystal is used to keep time and is temperature compensated inside the chip. A coin cell battery is plugged into the board to keep time even when the a feather battery is not connected. Data can be saved and read from SPI or I2C protocol communication.

Smart Rock Use Validation:
	The Smart Rock is using the Hypnos to keep temperature compensated time as well as storing all the data read by the sensors while in the stream bed. Smart Rock takes data every 20 minutes and this device allows such to happen. The RTC sends a square wave signal to a digital pin on the feather to wake the device from the power sleep to take data. Having this RTC allows for the device to keep time even in a low-power sleep mode.

More information about the Hypnos Board can be found [here](https://github.com/OPEnSLab-OSU/OPEnS-Lab-Home/wiki/Hypnos).
</details>

### Casing Design

The **outer case** is made of a piece of PVC with an union fitting at one end and a cap at the other. The union fitting and cap are mounted to the PVC using a layer of primer, then a layer of PVC cement. The smaller diameter, unthreaded, section of the union fitting is discarded and replaced with a circular piece of acrylic. This piece of acrylic has laser-cut holes for the sensors to be epoxied to make water-tight. The o-ring in the union fitting is coated in silicone grease to ensure a waterproof seal when the end of the union fitting is screwed back on with the acrylic. This modded union fitting design is used so that the electronics may be accessed and so that we can have the sensors protruding from one end without getting their wires twisted and tangled when the end is removed. 

SmartRock_Enclosure
_*Note this image is just the PVC enclosure._

The **internal structure** is made up of an acrylic platform that slides into the PVC enclosure. The electronics are then mounted this acrylic structure and slid into the case. Using the acrylic structure makes it easy to remove/access the electronics and holds everything in place. The electronics stack up on the slide allowing for a compact design.

SmartRock_AcrylicStructure
_*Note that the image above does not include electronics._

## Objectives

*  Low cost

*  Durable

*  Senses underwater pressure for depth

*  Senses stream temperature

*  Senses turbidity

*  Senses salinity

*  Battery life of at least 3 months

*  Clean and user-friendly electronics packaging

*  Keeps time for data collections

*  Connects to user easily

*  Waterproof

*  Remains in the location of placement

*  Safe for the environment

*  Withstand freezing temperatures

*  Easy internal access

*  Easy to retrieve and transport

## Outcomes

Current capabilities of Smart Rock sensors are depth measurement with accuracy within 0.13 mbar resolution as compared to an out of water pressure sensor, temperature accuracy of fewer than 0.01°C, turbidity measured in JTU, and a salinity measurement with an accuracy of less than 5 parts per million. Future developments will have flow sensing from the use of multiple high-accuracy pressure sensors. Battery life for Smart Rock is up to 3 months with low power sleep, a function that limits power usage from the device when dormant. This can be extended by taking data less often than once every 20 minutes. The device currently costs ~ $250 with these specifications and custom parts and takes about 10 hours to assemble and program.

<!--
### Field Test January 2020
![FieldTestphoto](https://user-images.githubusercontent.com/22950096/98614763-ef099000-22ad-11eb-8338-27d382e8bbb8.JPG)
![Turbidityresults](https://user-images.githubusercontent.com/46762333/80996902-72c15c00-8df5-11ea-9c2e-b5dc42e5fc3a.JPG)
![TDSResults](https://user-images.githubusercontent.com/46762333/80996988-91275780-8df5-11ea-907d-722e793f9230.JPG)
![BatteryResults](https://user-images.githubusercontent.com/46762333/80997060-ad2af900-8df5-11ea-9e59-19daa2c9bf59.JPG)
-->

## Future

The Smart Rock team is developing and revising the Smart Rock to improve the user experience and improve the quality of the Smart Rock. 

## Resource List

Link to Github page where code, design files, and guides can be found [here](https://github.com/OPEnSLab-OSU/SmartRock).

### Tutorials

Here are Resources from the 2019 CUAHSI workshop can be found [here](https://github.com/OPEnSLab-OSU/SmartRock/tree/master/Workshop%20Materials https://github.com/OPEnSLab-OSU/SmartRock/tree/master/Workshop%20Materials)

## Key Words
OPEnS, SmartRock, Smart Rock, Feather M0, Adalogger, Arduino, Stream, Water Monitor, Hydrological Data, Hydrological Monitoring, Pressure, Temperature, Electrical Conductivity, Dissolved Solids, Turbidity, seasonal streams, small streams

## References

Software

*  Fusion 360. (2018). San Rafael, California: Autodesk.

*  EAGLE CAD. (2018). San Rafael, California: Autodesk.

*  Arduino IDE. (2020). Turin, Italy: Arduino

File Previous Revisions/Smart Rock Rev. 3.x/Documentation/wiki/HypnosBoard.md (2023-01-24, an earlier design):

# Hypnos

## Hypnos Board

More information about the Hypnos Board can be found [Here](https://github.com/OPEnSLab-OSU/OPEnS-Lab-Home/wiki/Hypnos).

### Bill of Materials

Item Description | Notes | Quantity | Part Number | Dist. Website 
------ | ------ | ------ | ------- | ------
Hypnos Board | Data logging, system power, real time clock. | 1 | #### |  
Short Male Header | For Hypnos and Feather Boards | 1 | 3002 | [Adafruit](https://www.adafruit.com/product/3002)
Short Female Header | For Hypnos and EC Breakout Boards | 1 | 2940 | [Adafruit](https://www.adafruit.com/product/2940)

### Hypnos Assembly Guide

*If your Hypnos board already has short headers attached you are ready to go*

1. The female headers on the Hypnos board are going to accept the feather and face upward while the male headers are for the control side and stick out the bottom. Start by identifying which pair short and which long headers go where.

2. Start by soldering on the male headers to the PCB, it is recommended to use a template or other board to ensure the headers are straight and will align with the other boards. If you do not have a template solder a single pin and adjust to get them straight before soldering the rest.

3. Then flip over the board and repeat with the female headers, make sure they are flush and straight. Again, if a template or other board is available to help align pins it is recommended. 

4. Check that all soldering points are making good, complete contact and no two pins are shorting. Make extra sure of the ground pins, the ground plane helps cool those pins and can make it harder for the solder to flow there.

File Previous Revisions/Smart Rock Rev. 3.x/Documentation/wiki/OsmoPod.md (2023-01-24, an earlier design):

# OsmoPod

## OsmoPod V1.0 Sensor Package

<!-- More information about the OsmoPod can be found [Here](https://github.com/OPEnSLab-OSU/PNNLFluxV1/wiki/OsmoPod) -->

### Bill of Materials

Item Description | Notes | Quantity per 1 SR | Part Number | Dist. Website 
------ | ------ | ------ | ------- | ------
OsmoPod_Shield | Part laser cut from 1/16" extruded acrylic sheet. | 1 | #### | [McMasterCarr](https://www.mcmaster.com/8589K11/)
OsmoPod PCB |  | 1 | #### | 
10k Resistor | Soldered onto PCB | 2 | RR1220P-103-D | [Digi-Key](https://www.digikey.com/en/products/detail/susumu/RR1220P-103-D/432854)
100nF Capacitor | Soldered onto PCB | 1 | CL21F104ZBCNNNC | [Digi-key](https://www.digikey.com/en/products/detail/samsung-electro-mechanics/CL21F104ZBCNNNC/3889093)
MS5803 Sensor | Pressure and temperature sensor. | 1 | MS580302BA01-00 | [Digi-key](https://www.digikey.com/en/products/detail/te-connectivity-measurement-specialties/MS580302BA01-00/5277629)
Long Male Headers | EC probes for sensing. | 1 | 400 | [Adafruit](https://www.adafruit.com/product/400)
2-pin Male JST | EC probe wires. | 1 | B07449V33P | [Amazon](https://www.amazon.com/Shappy-Pieces-Connector-Silicone-Female/dp/B07449V33P/)
4-pin Male JST | I2C wires for MS5803. | 1 | 4330130986 | [Amazon](https://www.amazon.com/2-0MM-Female-Single-Connector-Wires/dp/B0732MMD7K)
3/8" Heat Shrink | about 1/2" long | 1 |  |

### OsmoPod Assembly Guide

Please read through the entire assembly guide before you begin.

1. Align the MS5803 with the indicator pin on the bottom of the sensor with the indicator trace on the PCB. Use a clamp (I use a small binder clip) to hold the sensor in place.

2. With the board in a vise and the sensor clamped in place, solder the sensor to the board. Use the exposed contacts on the side to ensure a solid connection.

3. Visually inspect the soldering points for a bad connection then test for shorts under the sensor using the continuity setting on a multi meter. The image below shows the circuit. If any of the pins are connected under the sensor or solder has bridged between traces add rosin and re-flow the solder to un-bridge those connections.

<p align="center">
    </a>
<p>

4. Flip the board over and solder the two surface mount resistors (R1 & R2) and one surface mount capacitor (C1) to the corresponding pads.

Solder R1, R2, C1

5. Take 3 long male headers and using pliers pull out the center header. Using a measuring device pull the two remaining headers so 10mm of the header is exposed from one side.

<p align="center">
    </a>
<p>

6. Install the headers on to the board in the GND and EC holes from the bottom of the board. Solder one of the headers in place, then make sure the plastic casing is flush with the PCB, if it is then solder the other header. If not re-flow the first one the straighten the probes.

7. Prep the wires and the board by slip a piece of heat shrink over the 2-pin JST for the EC and the 4-pin JST for the I2C for the MS5803. Then tin the backside of the EC probes so they can accept a wire.

8. Solder The EC wires to their posts with the red wire connecting to EC and the black wire to GND. For the I2C wires start with the black GND wire. The ground of the I2C should be soldered to the right pad of the capacitor next to the VCC hole with the wire pointing towards the inside of the PCB. After the ground is soldered the rest of the wires can be put in their corresponding holes and soldered in place.

Wire | Position 
------ | ------ 
EC - BLK | GND Post
EC - RED | EC Post
I2C - BLK | C1 Right Pad
I2C - RED | VCC Hole
I2C - WHT | SDA Hole
I2C -YLW | SCL Hole

9. Slide the heat shrink down over the exposed headers and organize the wires before gently heating the heat shrink sealing exposed headers.

10. With the epoxy mixed, less than 10mL needed, apply it carefully to the top of the PCB until the entire PCB is covered. Apply the OsmoPod_Shield to the epoxied PCB and apply pressure until the super glue has set Add more epoxy if a holes or gaps can let water in. Be careful to avoid getting epoxy in the MS5803 Sensor or on the EC Probes above the acrylic.  

11. Set the Osmopod in a location to dry overnight, make sure it is upright while drying.

The OsmoPod is ready to be tested and then installed on an acrylic face plate.

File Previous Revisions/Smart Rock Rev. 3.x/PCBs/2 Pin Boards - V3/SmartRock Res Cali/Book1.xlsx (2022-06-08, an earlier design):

SmartRock Resistor Calibration
 |  |  |  |  |  |  | Graphing the Data
Resistor Val (Byte) | Reading 1 | 2 | 3 | 4 | Ave | EC Solution | Res | DI | 23 | 84 | 447 | 1413
1 | 4151 | 2543 | 2543 | 2543 |  | DI | 1 | 2543 | 2538 | 2586.666667 | 2666.333333 | 2718.333333
11 | 2608 | 2820 | 2823 | 2824 |  |  | 11 | 2822.333333 | 2783.666667 | 3472.333333 | 4294 | 5505
21 | 2898 | 3113 | 3114 | 3115 |  |  | 21 | 3114 | 3032.333333 | 4435.666667 | 6100.333333 | 8692
31 | 3190 | 3408 | 3411 | 3412 |  |  | 31 | 3410.333333 | 3279.333333 | 5428.666667 | 7949.333333 | 11942.33333
41 | 3482 | 3709 | 3708 | 3709 |  |  | 41 | 3708.666667 | 3532 | 6443 | 9834 | 13631
51 | 3784 | 4008 | 4014 | 4017 |  |  | 51 | 4013 | 3780 | 7470 | 11710.66667 | 13627
61 | 4088 | 4321 | 4319 | 4319 |  |  | 61 | 4319.666667 | 4031.333333 | 8508.666667 | 13546 | 13624.33333
71 | 4399 | 4626 | 4625 | 4628 |  |  | 71 | 4626.333333 | 4278.666667 | 9559.666667 | 13632 | 13624.33333
81 | 4708 | 4937 | 4937 | 4938 |  |  | 81 | 4937.333333 | 4529.333333 | 10602 | 13632 | 13624.33333
91 | 5018 | 5246 | 5242 | 5242 |  |  | 91 | 5243.333333 | 4779.666667 | 11664 | 13632 | 13624.33333
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

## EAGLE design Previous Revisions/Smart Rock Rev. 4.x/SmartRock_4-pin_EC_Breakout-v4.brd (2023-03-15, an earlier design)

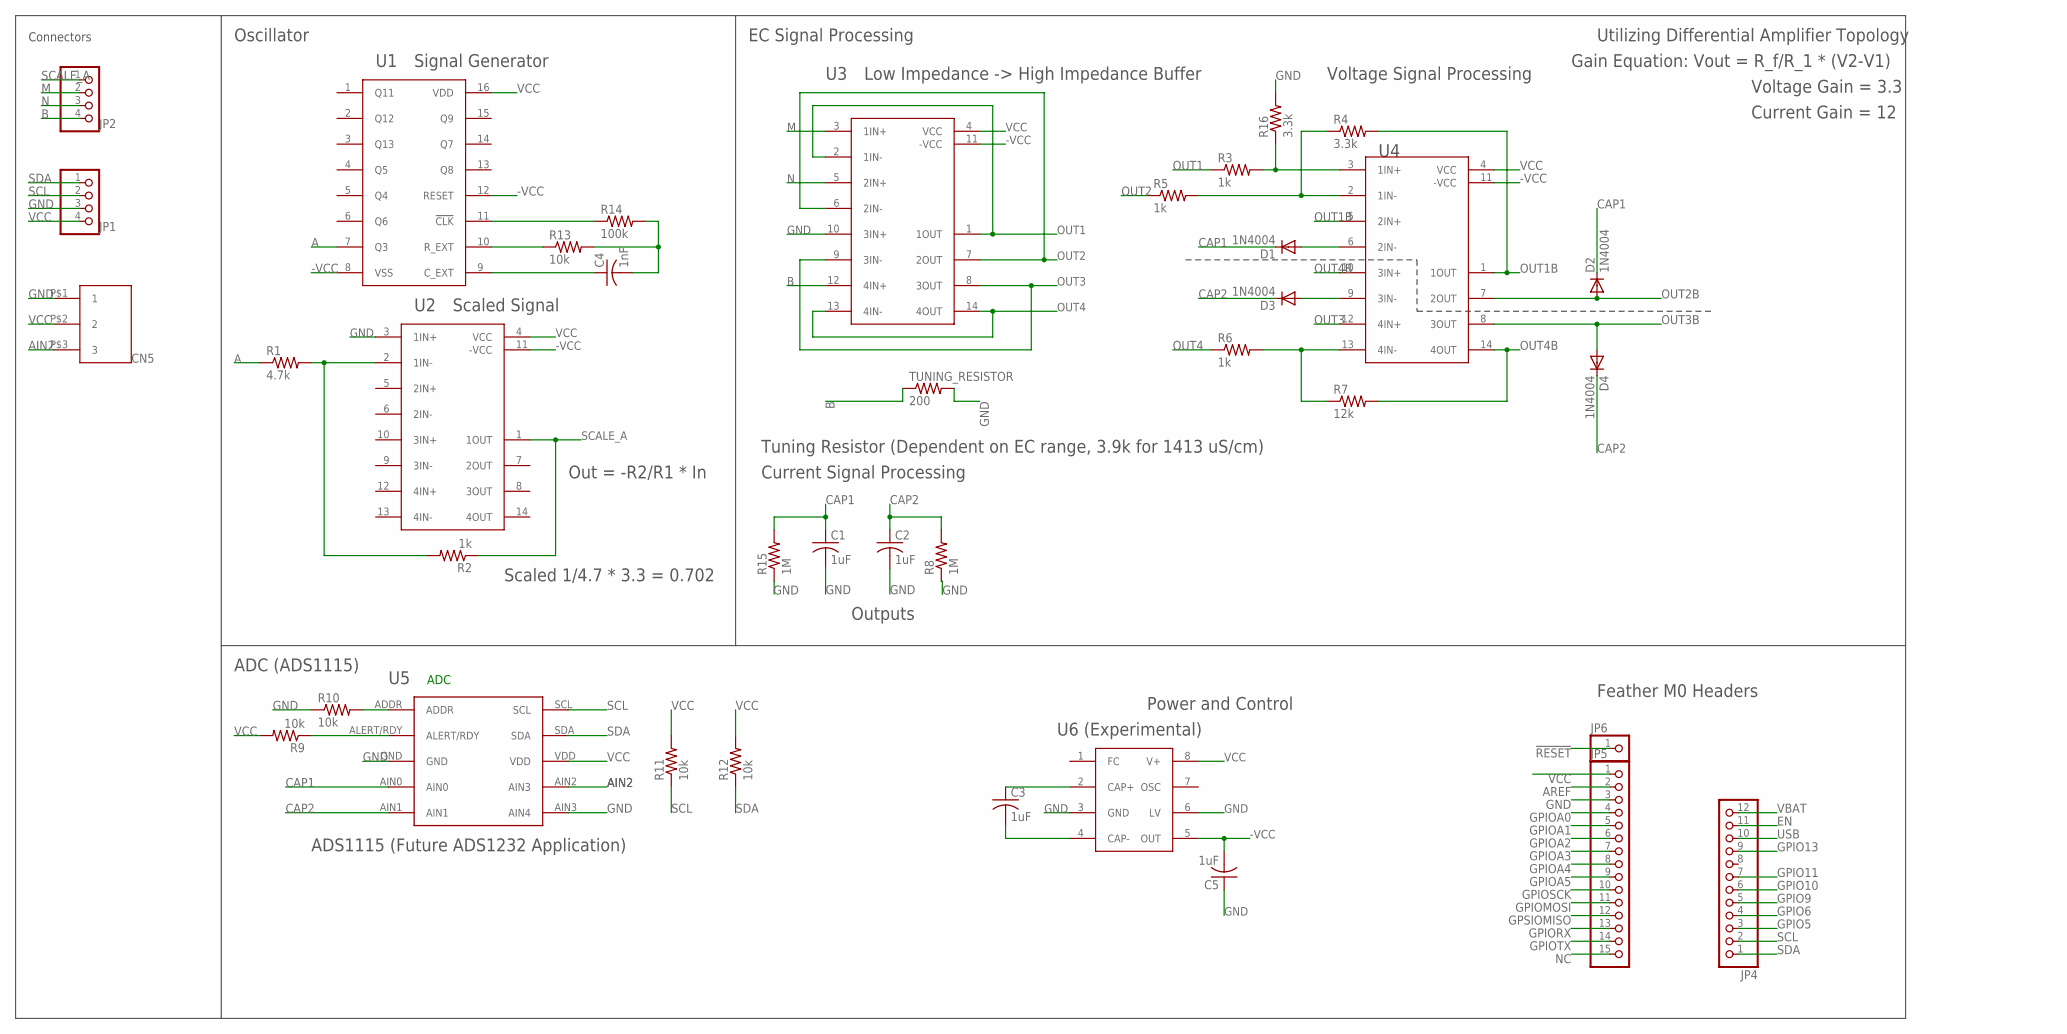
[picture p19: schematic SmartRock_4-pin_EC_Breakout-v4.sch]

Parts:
C1, C2, C3, C5: 1uF; C025-024X044
C4: 1nF; C1206
CN2: JST_3PIN_2MM
D1, D2, D3, D4: 1N4004; DO41-10
JP1, JP2: PINHD-1X4; 1X04
JP4: PINHD-1X12-CB; 1X12-CB
JP5: PINHD-1X15-CB; 1X15-CB
JP6: PINHD-1X1CB; 1X01-CLEANBIG
R1: 4.7k; M1206
R2, R3, R5, R6: 1k; M1206
R4, R16: 3.3k; M1206
R7: 12k; M1206
R8, R15: 1M; M1206
R9, R10, R11, R12, R13: 10k; M1206
R14: 100k; M1206
TUNING_RESISTOR: 200; M1206
U1: CD4060BPWR
U2, U3, U4: TL074CPWR; LT074CPWR
U5: ADS1115
U6+: MAX660MX/NOPB

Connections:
!RESET: JP6.1
-VCC: C5.2, U1.8 (VSS), U1.12 (RESET), U2.11 (-VCC), U3.11 (-VCC), U4.11 (-VCC), U6+.5 (OUT)
A: R1.1, U1.7 (Q3)
AIN2: CN2.P$3 (3), U5.AIN2 (AIN3)
AREF: JP5.2
B: JP2.4, TUNING_RESISTOR.1, U3.12 (4IN+)
CAP1: C1.1, D1.C, D2.C, R15.2, U5.AIN0
CAP2: C2.1, D3.C, D4.C, R8.2, U5.AIN1
EN: JP4.11
GND: C1.2, C2.2, C5.1, CN2.P$1 (1), JP1.3, JP5.3, R8.1, R10.1, R15.1, R16.2, TUNING_RESISTOR.2, U2.3 (1IN+), U3.10 (3IN+), U5.AIN3 (AIN4), U5.GND, U6+.3 (GND), U6+.6 (LV)
GPIO5: JP4.3
GPIO6: JP4.4
GPIO9: JP4.5
GPIO10: JP4.6
GPIO11: JP4.7
GPIO13: JP4.9
GPIOA0: JP5.4
GPIOA1: JP5.5
GPIOA2: JP5.6
GPIOA3: JP5.7
GPIOA4: JP5.8
GPIOA5: JP5.9
GPIOMOSI: JP5.11
GPIORX: JP5.13
GPIOSCK: JP5.10
GPIOTX: JP5.14
GPSIOMISO: JP5.12
M: JP2.2, U3.3 (1IN+)
N: JP2.3, U3.5 (2IN+)
unnamed: R3.2, R16.1, U4.3 (1IN+)
unnamed: R4.1, R5.2, U4.2 (1IN-)
unnamed: R1.2, R2.2, U2.2 (1IN-)
unnamed: D1.A, U4.6 (2IN-)
unnamed: R6.2, R7.1, U4.13 (4IN-)
unnamed: D3.A, U4.9 (3IN-)
unnamed: C3.1, U6+.2 (CAP+)
unnamed: C3.2, U6+.4 (CAP-)
unnamed: C4.1, U1.9 (C_EXT)
unnamed: R13.1, U1.10 (R_EXT)
unnamed: R14.1, U1.11 (!CLK)
unnamed: R10.2, U5.ADDR
unnamed: R9.1, U5.ALERT/RDY
unnamed: C4.2, R13.2, R14.2
NC: JP5.15
OUT1: R3.1, U3.1 (1OUT), U3.2 (1IN-)
OUT1B: R4.2, U4.1 (1OUT), U4.5 (2IN+)
OUT2: R5.1, U3.6 (2IN-), U3.7 (2OUT)
OUT2B: D2.A, U4.7 (2OUT)
OUT3: U3.8 (3OUT), U3.9 (3IN-), U4.12 (4IN+)
OUT3B: D4.A, U4.8 (3OUT)
OUT4: R6.1, U3.13 (4IN-), U3.14 (4OUT)
OUT4B: R7.2, U4.10 (3IN+), U4.14 (4OUT)
SCALE_A: JP2.1, R2.1, U2.1 (1OUT)
SCL: JP1.2, JP4.2, R11.1, U5.SCL
SDA: JP1.1, JP4.1, R12.1, U5.SDA
USB: JP4.10
VBAT: JP4.12
VCC: CN2.P$2 (2), JP1.4, JP5.1, R9.2, R11.2, R12.2, U1.16 (VDD), U2.4 (VCC), U3.4 (VCC), U4.4 (VCC), U5.VDD, U6+.8 (V+)

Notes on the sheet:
Oscillator
ADC (ADS1115)
Power and Control
ADC
Connectors
EC Signal Processing
Signal Generator
Scaled Signal
Out = -R2/R1 * In
Scaled 1/4.7 * 3.3 = 0.702
Low Impedance -> High Impedance Buffer
Voltage Signal Processing
Current Signal Processing
Outputs
Tuning Resistor (Dependent on EC range, 3.9k for 1413 uS/cm)
Utilizing Differential Amplifier Topology
Gain Equation: Vout = R_f/R_1 * (V2-V1)
Voltage Gain = 3.3
Current Gain = 12
ADS1115 (Future ADS1232 Application)
Feather M0 Headers
U6 (Experimental)
CN5

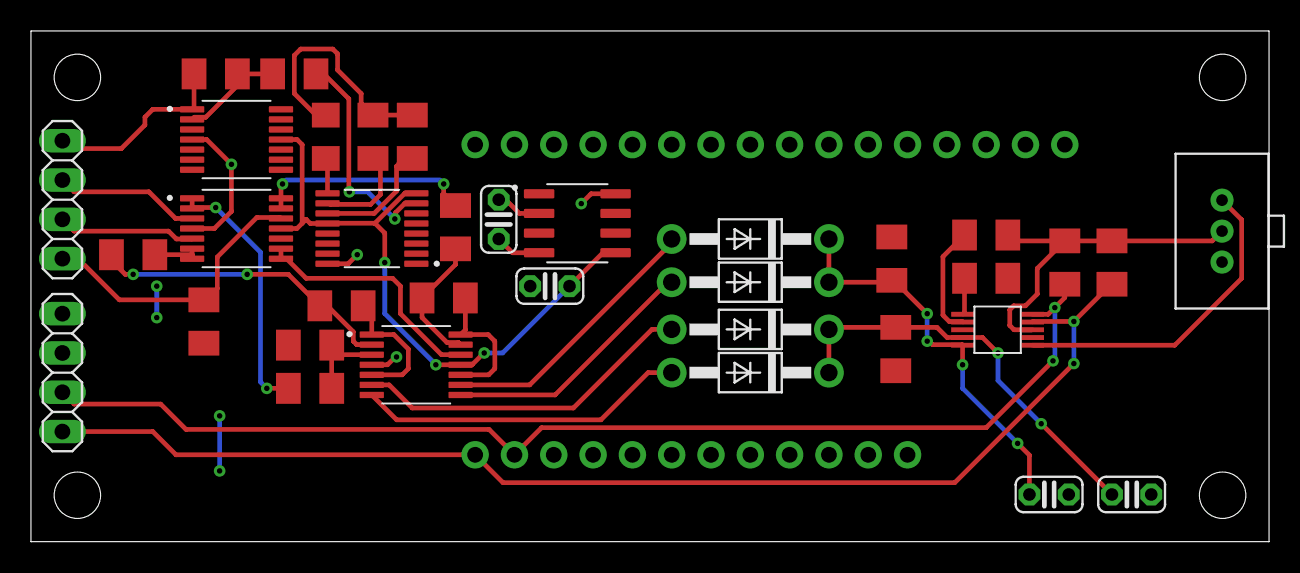
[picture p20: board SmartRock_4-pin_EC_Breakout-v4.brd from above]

Board: 2 copper layers, 80.0 x 33.0 mm, 38 parts (0 on the bottom side), 35 nets.

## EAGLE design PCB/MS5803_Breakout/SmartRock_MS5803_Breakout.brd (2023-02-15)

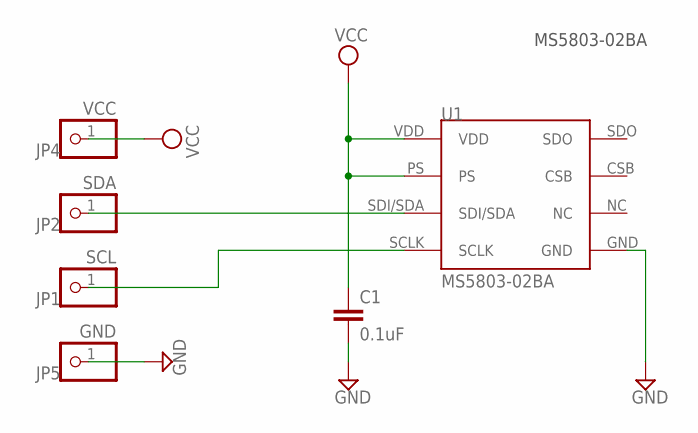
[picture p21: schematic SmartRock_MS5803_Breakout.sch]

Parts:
C1: 0.1uF; C0805
JP1: SCL; 1X01
JP2: SDA; 1X01
JP4: VCC; 1X01
JP5: GND; 1X01
U1: MS5803-02BA

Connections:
GND: C1.2, JP5.1, U1.GND
unnamed: JP2.1, U1.SDI/SDA
unnamed: JP1.1, U1.SCLK
VCC: C1.1, JP4.1, U1.PS, U1.VDD

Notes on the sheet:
MS5803-02BA

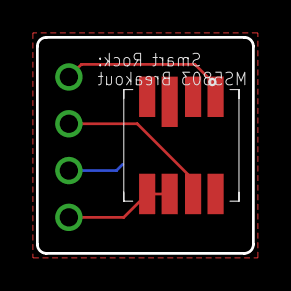
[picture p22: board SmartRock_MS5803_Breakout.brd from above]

Board: 2 copper layers, 12.0 x 12.0 mm, 6 parts (1 on the bottom side), 4 nets.

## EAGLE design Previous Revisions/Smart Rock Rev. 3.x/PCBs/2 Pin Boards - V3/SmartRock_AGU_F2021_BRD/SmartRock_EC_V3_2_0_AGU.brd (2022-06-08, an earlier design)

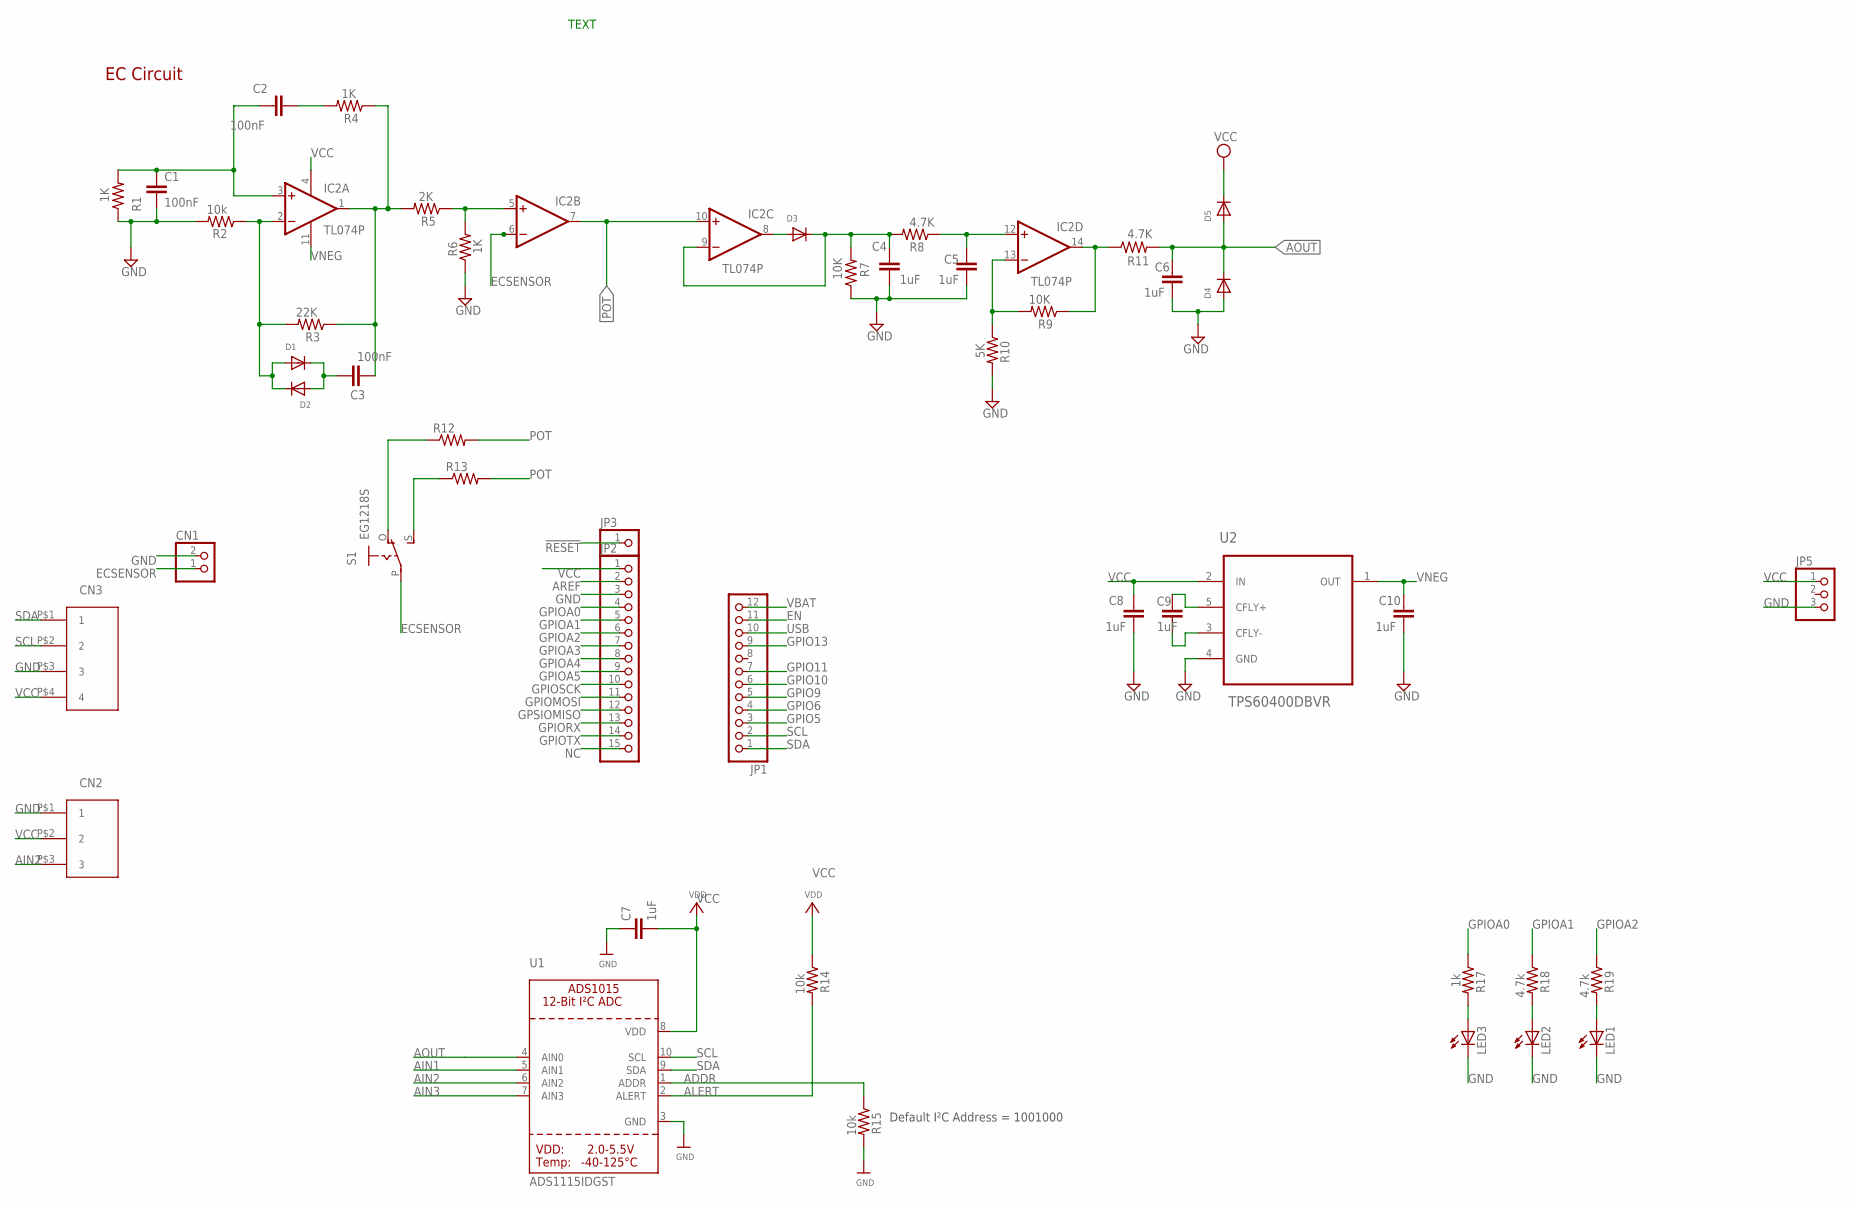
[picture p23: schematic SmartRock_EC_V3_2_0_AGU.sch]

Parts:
C1, C2, C3: 100nF; C1206
C4, C5, C6, C7, C8, C9, C10: 1uF; C1206
CN1: JST_2PIN-THM; JST-PH-2-THM
D1, D2, D3, D4, D5: DIODEDO-1N4148; DO-1N4148
IC2: TL074P; DIL14
JP1: PINHD-1X12-CB; 1X12-CB
JP2: PINHD-1X15-CB; 1X15-CB
JP3: PINHD-1X1CB; 1X01-CLEANBIG
JP5: PINHD-1X3CB; 1X03-CLEANBIG
LED1, LED2, LED3: LEDSMT1206; 1206
R1, R4, R6: 1K; R1206
R2, R14, R15: 10k; R1206
R3: 22K; R1206
R5: 2K; R1206
R7, R9: 10K; R1206
R8, R11: 4.7K; R1206
R10: 5K; R1206
R12, R13: R-US_0204/7; 0204/7
R17: 1k; R1206
R18, R19: 4.7k; R1206
S1: EG1218S; EG1218
U1: ADS1115IDGST; MSOP10
U2: TPS60400DBVR; SOT95P280X145-5N
U$7: JST_4PIN_2MM
U$9: JST_3PIN_2MM

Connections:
!RESET: JP3.1
ADDR: R15.1, U1.1 (ADDR)
AIN1: U1.5 (AIN1)
AIN2: U1.6 (AIN2), U$9.P$3 (3)
AIN3: U1.7 (AIN3)
ALERT: R14.2, U1.2 (ALERT)
AOUT: C6.2, D4.C, D5.A, R11.2, U1.4 (AIN0)
AREF: JP2.2
ECSENSOR: CN1.1 (2), IC2.6 (-IN), S1.P
EN: JP1.11
GND: C1.2, C4.1, C5.1, C6.1, C7.1, C8.1, C10.1, CN1.2 (1), D4.A, JP2.3, JP5.3, LED1.C, LED2.C, LED3.C, R1.1, R2.2, R6.1, R7.1, R10.2, R15.2, U1.3 (GND), U2.4 (GND), U$7.P$3 (3), U$9.P$1 (1)
GPIO5: JP1.3
GPIO6: JP1.4
GPIO9: JP1.5
GPIO10: JP1.6
GPIO11: JP1.7
GPIO13: JP1.9
GPIOA0: JP2.4, R17.1
GPIOA1: JP2.5, R18.1
GPIOA2: JP2.6, R19.1
GPIOA3: JP2.7
GPIOA4: JP2.8
GPIOA5: JP2.9
GPIOMOSI: JP2.11
GPIORX: JP2.13
GPIOSCK: JP2.10
GPIOTX: JP2.14
GPSIOMISO: JP2.12
unnamed: C1.1, C2.1, IC2.3 (+IN), R1.2
unnamed: C2.2, R4.2
unnamed: C3.2, IC2.1 (OUT), R3.1, R4.1, R5.2
unnamed: D1.A, D2.C, IC2.2 (-IN), R2.1, R3.2
unnamed: IC2.5 (+IN), R5.1, R6.2
unnamed: R13.1, S1.S
unnamed: R12.1, S1.O
unnamed: C3.1, D1.C, D2.A
unnamed: C4.2, D3.C, IC2.9 (-IN), R7.2, R8.2
unnamed: D3.A, IC2.8 (OUT)
unnamed: C5.2, IC2.12 (+IN), R8.1
unnamed: IC2.13 (-IN), R9.2, R10.1
unnamed: IC2.14 (OUT), R9.1, R11.1
unnamed: LED3.A, R17.2
unnamed: LED2.A, R18.2
unnamed: LED1.A, R19.2
unnamed: C9.2, U2.5 (CFLY+)
unnamed: C9.1, U2.3 (CFLY-)
NC: JP2.15
POT: IC2.7 (OUT), IC2.10 (+IN), R12.2, R13.2
SCL: JP1.2, U1.10 (SCL), U$7.P$2 (2)
SDA: JP1.1, U1.9 (SDA), U$7.P$1 (1)
USB: JP1.10
VBAT: JP1.12
VCC: C7.2, C8.2, D5.C, IC2.4 (V+), JP2.1, JP5.1, R14.1, U1.8 (VDD), U2.2 (IN), U$7.P$4 (4), U$9.P$2 (2)
VNEG: C10.2, IC2.11 (V-), U2.1 (OUT)

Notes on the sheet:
EC Circuit
Default I²C Address = 1001000
CN2
CN3
TEXT

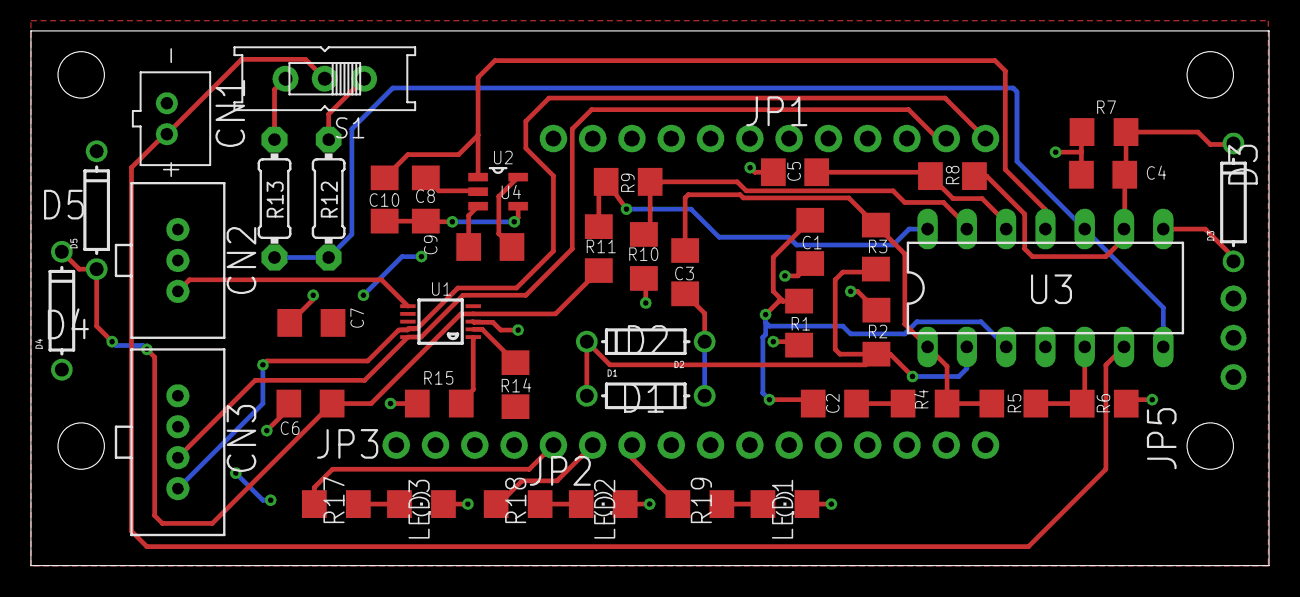
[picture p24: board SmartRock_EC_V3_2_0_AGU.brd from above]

Board: 2 copper layers, 80.0 x 34.6 mm, 47 parts (0 on the bottom side), 32 nets.

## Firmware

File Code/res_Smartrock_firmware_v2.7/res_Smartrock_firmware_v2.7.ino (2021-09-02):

 ///////////////////////////////////////////////////////////////////////////////

// This code is for the OPEnS Lab Smart Rock and Smart Rock Beta Group

// Includes
// - SD
// - DS3231 RTC
// - Deep Sleep functionality thanks to Hypnos (link below for more information)
// - EC
// - Turbidity
// - Pressure
// - Temp

// Further details about the Hypnos board can be found here:
// https://github.com/OPEnSLab-OSU/OPEnS-Lab-Home/wiki/Hypnos

///////////////////////////////////////////////////////////////////////////////

#include <Loom.h>
#include <ArduinoJson.h>
#include <SdFat.h>
#include <Wire.h>

// Include configuration
const char* json_config = 
#include "config.h"
;

// Set enabled modules
LoomFactory<
  Enable::Internet::Disabled,
  Enable::Sensors::Enabled,
  Enable::Radios::Enabled,
  Enable::Actuators::Enabled,
  Enable::Max::Enabled
> ModuleFactory{};

LoomManager Loom{ &ModuleFactory };
DynamicJsonDocument doc(1024);

const int switchPin = 19;
int switchPos = 0;

int secs = 0;
int mins = 0;
int hours = 0;
int days = 0;
byte res = 0;

volatile bool rtc_flag = false;

void wakeISR_RTC() {
  // disable the interrupt
  detachInterrupt(12);
  rtc_flag = true;
}

//custom function from Cameron of PNNL to make use of variable resistor
//found on newest hydro board PCB
void send_data(byte addr, byte data){
  Wire.beginTransmission(addr);
  Wire.write(data);
  Wire.endTransmission(true);
}

//custom function to read specified operation interval file from SD
void readOpInt(char* opInt){

  SdFat sd;
  digitalWrite(8, HIGH);
  bool sd_found = sd.begin(SD_CS, SD_SCK_MHZ(50));
  if (sd_found){
    LPrintln("Found SD");
  } else {
    LPrintln("SD Not Found");
  }
  
  File file = sd.open(opInt);
  if (file){
    LPrintln("File is good");
  }
  DeserializationError error = deserializeJson(doc, file);
  
  if (error) { // Make sure json was valid
    LPrintln("deserializeJson() failed: ", error.c_str());
  }
  
  serializeJsonPretty(doc, Serial);
  JsonObject json = doc.as<JsonObject>();

  //This will set the time values
  //based on the values parsed from .txt file on SD
  secs = json["seconds"];
  mins = json["minutes"];
  hours = json["hours"];
  days = json["days"];

  res = json["res"];

}

void setup() 
{
  //sets our switchPin as INPUT
  pinMode(switchPin, INPUT);
  
  // Needs to be done for Hypno Board
  pinMode(5, OUTPUT);   // Enable control of 3.3V rail 
  pinMode(6, OUTPUT);   // Enable control of 5V rail 
  pinMode(12, INPUT_PULLUP);    // Enable waiting for RTC interrupt, MUST use a pullup since signal is active low
  pinMode(13, OUTPUT);

  //digitalWrite(switchPin, HIGH);
  //See Above
  digitalWrite(5, LOW); // Enable 3.3V rail
  digitalWrite(6, HIGH);  // Enable 5V rail
  digitalWrite(13, LOW);

  //required for variable resistor use
  Wire.begin();

  Loom.begin_serial(true);
  Loom.parse_config(json_config);
  Loom.print_config();


 //Got rid of the physical switch, so just have it read
  //from the custom file
  switchPos = digitalRead(switchPin);
  char* customOp = "customOperationInterval.txt";
  readOpInt(customOp);
  
//  if (switchPos == HIGH) {
//    char* defaultOp = "operationInterval.txt";
//    readOpInt(defaultOp);
//    
//  }else{
//      char* customOp = "customOperationInterval.txt";
//      readOpInt(customOp);
//  }
  
  // Register an interrupt on the RTC alarm pin
  Loom.InterruptManager().register_ISR(12, wakeISR_RTC, LOW, ISR_Type::IMMEDIATE);

  LPrintln("\n ** Setup Complete ** ");
  Serial.flush();
}

//byte res = 10; // EC Resolution anything larger than 0

void loop() 
{
  
  digitalWrite(5, LOW); // Disable 3.3V rail
  digitalWrite(6, HIGH);  // Disable 5V rail
  digitalWrite(13, HIGH);

  // As it turns out, if the SD card is initialized and you change
  // the states of the pins to ANY VALUE, the SD card will fail to
  // write. As a result, we ensure that the board has been turned
  // off at least once before we make any changes to the pin states
  if (rtc_flag) {
    pinMode(23, OUTPUT);
    pinMode(24, OUTPUT);
    pinMode(10, OUTPUT);

    delay(1000);

    Loom.power_up();
  }


  //send data to address of I2C
  send_data(0x2E, res); // set resistance in EC circuit
  Serial.print(res);

  //aim to 10000 for max EC value for solution then calibrate.
    
  Loom.measure();
  Loom.package();
  Loom.display_data();
  Loom.SDCARD().log();

  // set the RTC alarm to a custom duration specified by 
  // the user via operationInterval.txt or customOperationInterval.txt 
  // depending on switch position
  Loom.InterruptManager().RTC_alarm_duration(TimeSpan(days,hours,mins,secs));
  Loom.InterruptManager().reconnect_interrupt(12);

  digitalWrite(13, LOW);
  digitalWrite(5, HIGH); // Enable 3.3V rail
  digitalWrite(6, LOW);  // Enable 5V rail
  pinMode(23, INPUT);
  pinMode(24, INPUT);
  pinMode(10, INPUT);

  // Sleep Manager autmatically calls power_down on every sensor before sleeping
  // And power_up after waking.

  rtc_flag = false;
  Loom.SleepManager().sleep();
  while (!rtc_flag);
}

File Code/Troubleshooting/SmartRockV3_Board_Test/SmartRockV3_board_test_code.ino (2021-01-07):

///////////////////////////////////////////////////////////////////////////////

// This is simple one of the simplest examples of using Loom. The code used
// in this example shows up in the majority of other cases as well. 

// The include, config, LoomFactory, and LoomManager are typically used in
// this way.

// The setup almost always includes what is in this example, and in many 
// cases, no further setup is necessary

// The loop is also the start of what most cases use, namely: measure,
// package, display, and wait (according to 'interval' in the config).
// Other examples simply build off of this sequence

// Documentation for ADS1115: https://openslab-osu.github.io/Loom/doxygenV2/html/class_loom___a_d_s1115.html

///////////////////////////////////////////////////////////////////////////////

#include <Loom.h>


// Include configuration
const char* json_config = 
#include "config.h"
;

// Set enabled modules
LoomFactory<
	Enable::Internet::Disabled,
	Enable::Sensors::Enabled,
	Enable::Radios::Disabled,
	Enable::Actuators::Disabled,
	Enable::Max::Disabled
> ModuleFactory{};

LoomManager Loom{ &ModuleFactory };


//pins for the LEDs
int LED1_pin = 5;
int LED2_pin = 6;
int LED3_pin = 10;


//pin for the switch
const int switchPin = 9;
int switchPos = 0;




void setup() 
{

  pinMode(switchPin, INPUT);
  pinMode(LED1_pin, OUTPUT);
  pinMode(LED2_pin, OUTPUT);
  pinMode(LED3_pin, OUTPUT);

  
   
	Loom.begin_serial(true);
	Loom.parse_config(json_config);
	Loom.print_config();

	LPrintln("\n ** Setup Complete ** ");
  Serial.flush();
}


void loop() 
{

  switchPos = digitalRead(switchPin);

  if(switchPos == HIGH){

    LPrintln("\n***************LED STATUS***************");
    LPrintln("**********************************\n");
    digitalWrite(LED1_pin, HIGH);
    delay(100);
    digitalWrite(LED1_pin, LOW);
    delay(100);
    LPrintln("\n LED 1 Working!");
    
    digitalWrite(LED2_pin, HIGH);
    delay(100);
    digitalWrite(LED2_pin, LOW);
    delay(100);
    LPrintln("\n LED 2 Working!");
    
    digitalWrite(LED3_pin, HIGH);
    delay(100);
    digitalWrite(LED3_pin, LOW);
    delay(100);
    LPrintln("\n LED 3 Working!");
    LPrintln("\n***************************************\n");

    LPrintln("\n***************SWITCH STATUS***************");
    LPrintln("********************************************\n");
    LPrintln("SWITCH == HIGH");
    LPrintln("\n******************************************\n");
    
    
  }else{

    LPrintln("\n***************LED STATUS***************");
    LPrintln("*****************************************\n");
    digitalWrite(LED1_pin, LOW);
    delay(100);
    LPrintln("\n LED 1 is OFF!");
    digitalWrite(LED2_pin, LOW);
    delay(100);
    LPrintln("\n LED 2 is OFF!");
    digitalWrite(LED3_pin, LOW);
    delay(100);
    LPrintln("\n LED 3 is OFF!");
    LPrintln("\n*****************************************\n");

    LPrintln("\n***************SWITCH STATUS***************");
    LPrintln("********************************************\n");
    LPrintln("SWITCH == LOW");
    LPrintln("\n******************************************\n");
    
  }
   
	Loom.measure();
	Loom.package();
	Loom.display_data();
	Loom.pause();

}

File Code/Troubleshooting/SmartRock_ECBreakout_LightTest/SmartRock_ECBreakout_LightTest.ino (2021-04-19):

/*
  Basically a Blink Test for the Smart Rock to Ensure the Lights are Working.
*/

// Define LED Pins
int GLED = 14; // Green LED
int OLED = 15; // Orange LED
int RLED = 16; // Red LED

void setup() {
  // initialize the leds as outputs.
  pinMode(GLED, OUTPUT);
  pinMode(OLED, OUTPUT);
  pinMode(RLED, OUTPUT);

}

void loop() {
  digitalWrite(GLED, HIGH);   // turn the Green LED on
  delay(1000);                       // wait for a second
  digitalWrite(GLED, LOW);    // turn the Green LED off
  delay(1000);                       // wait for a second
  
  digitalWrite(OLED, HIGH);   // turn the Orange LED on
  delay(1000);                       // wait for a second
  digitalWrite(OLED, LOW);    // turn the Orange LED off
  delay(1000);                       // wait for a second
  
  digitalWrite(RLED, HIGH);   // turn the Red LED on
  delay(1000);                       // wait for a second
  digitalWrite(RLED, LOW);    // turn the Red LED off
  delay(1000);                       // wait for a second
}

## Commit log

2019-09-23 HydroPCB added
    [HydroPCB.brd, HydroPCB.sch]
2019-10-25 Loom w/config 2.5
    Wifi m0, hypnos, 3 analog, 1 i2c sensor
2020-02-03 Add MS5803 pcb files
    [SmartRockMS5803.brd, SmartRockMS5803.sch]
2020-09-03 edits after workshop
    [Inside (1).stl, Outside (1).stl]
2020-09-03 workshop materials added
    [Bill of Materials for Cuahsi.xlsx, Inside (1).stl, Inside.stl, Outside (1).stl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]
2020-11-11 Added laser cut parts to github
    Added laser cut parts and made a central folder for 3d printed parts.
    [Inside.stl, Outside.stl]
2020-12-08 Re-organized File Structure
    Re-organized the files so that there is destinations for the new content as it is created.
    [Battery_Mount V11.stl, Electronics_Mount v15.dxf, HydroPCBedits.brd, HydroPCBedits.sch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]
2020-12-09 Update Laser Cut files
    [Electronics_Mount v26.dxf, MD5803_Shield v13.dxf, Sensor_Mount v12.dxf, Sled_Base v27.dxf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]
2020-12-09 Fix README for the laser cut files
2020-12-11 Updated Part Files
    Updated parts after prototyping.
    [Battery_Mount V11.stl, Battery_Mount v17.stl, EC Feather Breakout 3.2.brd, EC Feather Breakout 3.2.sch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]
2020-12-12 Update README.md
    Work done to the assembly guide.
2020-12-16 added test code files for the Smart Rock v3 board
2020-12-21 Update Part files and READMEs
    [Rail_Inside v10.stl, Rail_Inside v15.stl, Rail_Outside v11.stl, Rail_Outside v12.stl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]
2020-12-22 Update Readme
    Added hypnos assembly guide and corrections to the main page.
2020-12-26 Update README Fix part naming
    [Acrylic_Faceplate v16.dxf]
2021-01-15 Operation interval through external txt file
    With this version of the firmware, users are able to change the operation interval of the Smart Rock through a .txt file named: operationInterval.txt
    Users now do not have to re-upload their arduino code every time they want to make a small change to the operation interval.
2021-02-12 cleaner code of v2.6_varRes
    Cleaned up the code considerably and was able to implement picking between 2 different operation interval .txt files. Setting the switch on the Smart Rock to HIGH will read the operation interval val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
2021-02-12 Update README.md
    added Firmware section for current version
2021-02-16 fix naming
    [SR_Faceplate v16.dxf]
2021-04-17 Breakout Board Fix
    [SmartRock_EC.brd, SmartRock_EC.sch]
2021-04-18 Update 3D Prints
    [Battery_Mount v17.stl, Battery_Mount v18.stl, Rail_Inside v15.stl, Rail_Inside v16.stl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]
2021-04-19 Updated Board and Code
    [SmartRock_EC.brd, SmartRock_EC.sch]
2021-04-23 New Smart Rock Code
    Also added low tolerance print option.
    [Rail_Inside v18.stl]
2021-05-23 Updated PCBs
    Organized and updated PCB files.
    [SmartRock_EC.brd, SmartRock_EC.sch, SmartRock_OsmoPod.brd, SmartRock_OsmoPod.sch]
2021-09-21 Add second workshop to Github
    [Combined_sensor_calculations_CUAHSI_SmartRock_2020.xlsx, EC_calibration_CUAHSI_SmartRock_2020.xlsx, EC_example_file_CUAHSI_SmartRock_2020.csv, Pressure_tempera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]
2022-02-25 Add workshop materials
    [Combined_sensor_calculations_CUAHSI_SmartRock_2021.xlsx, EC_calibration_CUAHSI_SmartRock_2021.xlsx, Pressure_temperature_validation_CUAHSI_SmartRock_2021.xlsx]
2022-06-08 Updating Electronics Documents - PCB design additions
    [Book1.xlsx, SmartRock_EC.brd, SmartRock_EC.sch, SmartRock_EC_V3_2_0_AGU.brd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]
2023-01-24 Smart Rock V4 Transition Start
    [Battery_Mount v18.stl, Book1.xlsx, Electronics_Mount v26.dxf, OsmoPod_Shield v13.dxf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]
2023-01-24 Exported internal support file
    [SR_InternalSupport_v13_1x3.5mm.dxf]
2023-01-24 Added SR 4.0 Laser Cut Parts
    [SM_CapWrench_v7_1x6mm.dxf, SR_MountPlate_v30_1x3.5mm.dxf, SR_SensorFacePlate_v24_1x6mm.dxf, SR_StructureArm_v16_1x3.5mm.dxf]
2023-02-15 Add MS5803 Breakout Board
    [SmartRock_MS5803_Breakout.brd, SmartRock_MS5803_Breakout.sch]
2023-02-16 Board Rev. 5 Progress
    getting closer to a finished board
    [SmartRock-4-pin-EC-v4.3.3.brd, SmartRock_4-pin_EC_Breakout-v5.brd, SmartRock_4-pin_EC_Breakout-v5.sch]
2023-02-23 Fit 4-pin on two layers
    New circuit is on two layers now, layout done. I need to go over it again and get the trace lengths to match where needed and I need to check for physical interference. So close I can smell it.
    [SmartRock_4-pin_EC_Breakout-v5.brd]
2023-03-15 Fix cap positons
    [SmartRock_4-pin_EC_Breakout-v5.brd]
2023-04-11 Added slit in "Internal Support" and tab in "Mount Plate"
    [SR_InternalSupport_v17_1x3.5mm.dxf, SR_MountPlate_v34_1x3.5mm.dxf, SR_SensorFacePlate_v28_1x6mm.dxf, SR_SensorShield_v12_1x3.5mm.dxf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]
2023-08-07 changed width
    [SR_InternalSupport_v17_1x3mm.dxf, SR_MountPlate_v34_1x3mm.dxf, SR_SensorFacePlate_v28_1x6.35mm.dxf, SR_SensorShield_v12_1x3mm.dxf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]
2023-09-05 added new structure design with longer stuff
    [SR_InternalSupport_v27_1x3mm.dxf, SR_MountPlate_v42_1x3mm.dxf, SR_SensorFacePlate_v48_1x9.125mm.dxf, SR_StructureArm_v31_1x3mm.dxf]
2024-05-22 10000mAh battery clearance and strap
    Changed tolerances to fit battery better, added strap to help secure battery
    [BlackTurbCap.stl, SR_InternalSupport_v29_1x3mm.dxf, SR_MountPlate_v42_1x3mm.dxf, SR_MountPlate_v45_1x3mm.dxf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]
2025-05-13 Lab Tested Stable, EC and Turbidity not calibrated
